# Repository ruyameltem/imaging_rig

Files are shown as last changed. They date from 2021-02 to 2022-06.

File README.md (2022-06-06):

<h1 style="text-align: justify;"><strong>imaging Rig for Microfluidic blood analysiS (RMS)</strong></h1>
<h2 style="text-align: center;">Lights, Camera, Action!</h2>
<p>Rise of the blood and plasma</p>

<p style="text-align: justify;"><strong>Developed by</strong> Edwards lab, University of Reading School of Pharmacy <a href="https://research.reading.ac.uk/biomedical-technology-lab/">Biomedical Technology Lab</a></p>

<p style="text-align: justify;">The imaging rig has been developed to quickly test platelet function for cardiovascular health and disease epidemiology.</p>

<p style="text-align: justify;">This project aims at developing new assays and miniaturised devices to measure the function of the blood cells involved in clotting and thrombus formation- platelets (thrombocytes). The micro capillary film containing small capillaries and made using a melt extrusion process is used to develop new ways of measuring platelet function. We have been testing new detection methods such as using the Raspberry Pi camera.</p>

<p style="text-align: justify;">This system can be used to measure the parameters of liquids such as density and viscosity. By taking time-lapse images, kinetic information of the fluid in the capillary can be obtained. In this way, it is a suitable device not only for blood studies, but also for anyone who wants to work with fluids.</p>

<p style="text-align: justify;">This research shall contribute to the improvement of a new generation with state-of-the-art but affordable point-of-care tests for global utilizations.</p>

<p>You can find the rig's <a title="Technical Specifications" href="https://gitlab.com/ruyameltem/imaging_rig/-/blob/master/Technical%20Specifications.pdf" target="_blank" rel="noopener">Technical Specifications</a></p>

<h3 style="text-align: justify;">Fundamental and 3D-printed parts</h3>
<p><strong>Before you begin,</strong> make sure you have all the necessary parts. You can find all the parts in the <a title="Bill of Materials" href="https://gitlab.com/ruyameltem/imaging_rig/-/blob/master/Bill%20of%20Materials.pdf" target="_blank" rel="noopener">Bill of Materials</a> list.</p>
<p>It is good to have basic skills to use Raspberry Pi, some wiring skills for electronic parts, and designing and printing skills for 3D-printed parts. Do not worry! You can gain skills by watching some short videos and browsing websites. Keep moving forward I added useful links for you. You only need to know how you can use the Raspberry Pi, which is a minicomputer and its pins, how you can wire the "black and red" cables and how to print the designs.</p>
<p>Make sure you have the necessary parts (camera, screen, power supply, SD card, optional: keyboard, mouse) to run the Raspberry pi.</p>
<p>Here are some useful links for Raspberry Pi: <a title="Getting started with Raspberry Pi" href="https://www.raspberrypi.com/dhttps://www.raspberrypi.com/documentation/computers/getting-started.htmlocumentation/computers/getting-started.html" target="_blank" rel="noopener">Getting started with Raspberry Pi</a>, <a title="Documentation: Raspberry Pi" href="https://www.raspberrypi.com/documentation/" target="_blank" rel="noopener">Documentation: Raspberry Pi</a>, <a title="Software: Raspberry Pi" href="https://www.raspberrypi.com/software/" target="_blank" rel="noopener">Software: Raspberry Pi</a></p> 

<p><strong>After collecting the fundamental parts,</strong> you will need to print the 3D printed parts. Download the STL files through the <a title="Design files - OpenSCAD" href="https://gitlab.com/ruyameltem/imaging_rig/-/tree/master/Design_files%20-%20OpenSCAD" target="_blank" rel="noopener">Design files - OpenSCAD</a> page.</p>

<p>You will need the nuts, bolts, etc. to assemble some of the parts. I printed 3D parts with Prusa i3 MK3. It is fine to use another 3D printer. You can tick the support option for some designs. You can change the layer size or any other settings. See below the settings I use:</p>

<p>printer settings</p>
<p>I used the black PLA filament to print all the parts. I just used transparent PLA filament for the test strip holder.</p>
<p>I designed and printed holders to attach all parts (battery, relay, etc.) to the aluminium extrusion. All are available on the design page.</p>
<p>If you have purchased the parts and printed what you need to print, now it is time to assemble them.</p>

<h3 style="text-align: justify;">Assembly Instructions</h3>
<h4 style="text-align: justify;">Assembling the V-Slot aluminium extrusions</h4>
<p>We used 4 20x20mm V-Slot linear rails to create the rectangle at the base. We used a 20x40mm extrusion to attach the servo motor, v-slot gantry plate kit, sample and test strip holders. We used a 20x80mm extrusion to fix the Pi camera and touchscreen. We wanted to be able to change the height of the camera when needed.</p>
<p>We used inside hidden corner, 90-degree cast corner, drop-in tee nuts and hex nuts to combine them. You can find the details in the bill of materials.</p>

<h4 style="text-align: justify;">Assembling the servo motor, gantry plate and strip holder</h4>
<p>The servo motor was attached to the 20x40mm aluminium extrusion by means of the servo bracket. An eccentric horn was placed on the servo in order to make the test strip holder rise and fall as the servo operated.</p>
<p>Servo is controlled by Raspberry Pi via servo six motor kit. The kit is powered by 4 AA batteries.</p>
<p>Useful link for servo six motor kit assembly instruction: <a title="Instructions: servo six board" href="https://cdn.shopify.com/s/files/1/0176/3274/files/instructions_servo_six.pdf?v=1589990518" target="_blank" rel="noopener">servo six board</a></p>

<p>Also, the stripwell holder is mounted on the extrusion. The holder fits a 1 x 12 Stripwell™ Microplate.</p>

<p>The gantry plate was placed on the extrusion so that it was on the upper part of the servo. In addition, the rack holder was mounted on the gantry plate to place the strip holder. Thus, the plate moves up and down by the servo so that it moves the holder.
Useful link for <a title="Gantry plate assembly" href="https://ooznest.co.uk/wp-content/uploads/2018/07/OX-Assembly-Manual.pdf">Gantry plate assembly instructions</a></p>

See figures:
<p>servo assembly</p>

<h4 style="text-align: justify;">Assembling the camera and touchscreen</h4>
<p>The V2 Pi camera was mounted on the Raspberry Pi camera medium plate V2. Following this, the plate was attached to the 20x80mm aluminium extrusion. In addition, the touch screen was attached to the same extrusion by means of 2 touch Pi mounts and 2 universal mounts. Raspberry Pi was mounted on the back of the screen via the Pi case.</p>
<p>Useful links for camera and screen assembly instructions: <a title="Getting started with 7&Prime; touchscreen" href="https://www.okdo.com/getting-started/get-started-with-7-touchscreen-for-raspberry-pi/" target="_blank" rel="noopener">Getting started with 7&Prime; touchscreen</a>, <a title="Getting started with picamera" href="https://projects.raspberrypi.org/en/projects/getting-started-with-picamera" target="_blank" rel="noopener">Getting started with picamera</a></p>

<h4 style="text-align: justify;">Assembling the light sources and relay</h4>
<p>The white LED strips were soldered to the plastic sheet with black and red wires and framed by 4 20x80mm aluminium extrusions. The black wire should be soldered to the minus and the red wire to the positive. 2 holes were drilled on the plastic sheets and the sheets were mounted on the extrusion with screws. The lightbox was also mounted on the main frame.</p>

<p>The light source is controlled by Raspberry Pi via relay.</p>
<p>Useful links for relay assembly instructions and LED wiring: <a title="Relay and Raspberry Pi" href="https://www.electronicshub.org/control-a-relay-using-raspberry-pi/#:~:text=Technically%20speaking%2C%20a%20relay%20is,with%20respect%20to%20Raspberry%20Pi." target="_blank" rel="noopener">Relay and Raspberry Pi</a>, <a title="LED strips" href="https://www.waveformlighting.com/home-residential/how-to-connect-an-led-strip-to-a-power-supply" target="_blank" rel="noopener">LED strips</a></p>

<p>Picture10led</p>

<h3 style="text-align: justify;">Run the Rig</h3>
</p>You only need to place your samples and microfluidic into the system. Then only you will need to run the script.</p>
</p>If you are wondering how the system works, check it out: <a title="Rig" href="https://gitlab.com/ruyameltem/imaging_rig/-/blob/master/Rig.mp4">Rig</a></p>

<p>A short video from an experiment: <a title="Performing an experiment" href="https://gitlab.com/ruyameltem/imaging_rig/-/blob/master/Performing%20an%20experiment.mp4">Performing an experiment</a></p>

<h3 style="text-align: justify;">Software</h3>

<p>To view, edit, and run a Python script, you can use the Thonny which is an integrated development environment (IDE). It is already pre-installed on the Raspberry Pi. Check out the link for the helpful video: <a title="Raspberry Pi OS - Get Started with Thonny IDE" href="https://www.youtube.com/watch?v=GssM7hkwJrc" target="_blank" rel="noopener">Raspberry Pi OS - Get Started with Thonny IDE</a></p>

<p>If you want to update Python and your Raspberry Pi, make sure you type and run the following separately in the command section:</p>
<p>1 - sudo apt update</p>
<p>2 - sudo apt full-upgrade</p>
<p>3 - sudo apt-get update</p>
<p>4 - sudo apt-get install python3</p> 

<p>Note: I did not install the Bullseye edition because the camera system has errors with the last update of Raspberry Pi. But if you want to install and update, you can get help from this video to solve the problem: <a title="Raspberry Pi OS Bullseye Update: New Features &amp; Camera Issues" href="https://www.youtube.com/watch?v=0kr_yS9OhLM" target="_blank" rel="noopener">Raspberry Pi OS Bullseye Update: New Features &amp; Camera Issues</a></p>

<p>If you want to use the scripts separately, there are separate scripts for recording video, controlling the LED with a relay, and taking time-lapse images with a date stamp.</p>
<p>But if you want to download and use it directly, the script file you will run is called "Imaging Rig".</p>
<p>Here are the Python scripts you need: <a title="Software" href="https://gitlab.com/ruyameltem/imaging_rig/-/tree/master/Software">Software</a></p>
<p>It is good to have basic Python skills to make some changes on the scripts.</p>

<p>For any questions, please contact me: <a title="r.sariyer@pgr.reading.ac.uk" href="mailto:r.sariyer@pgr.reading.ac.uk">r.sariyer@pgr.reading.ac.uk</a></p>

<h3 style="text-align: justify;">The Rig</h3>
<p style="text-align: justify;">The device is shown below.</p>
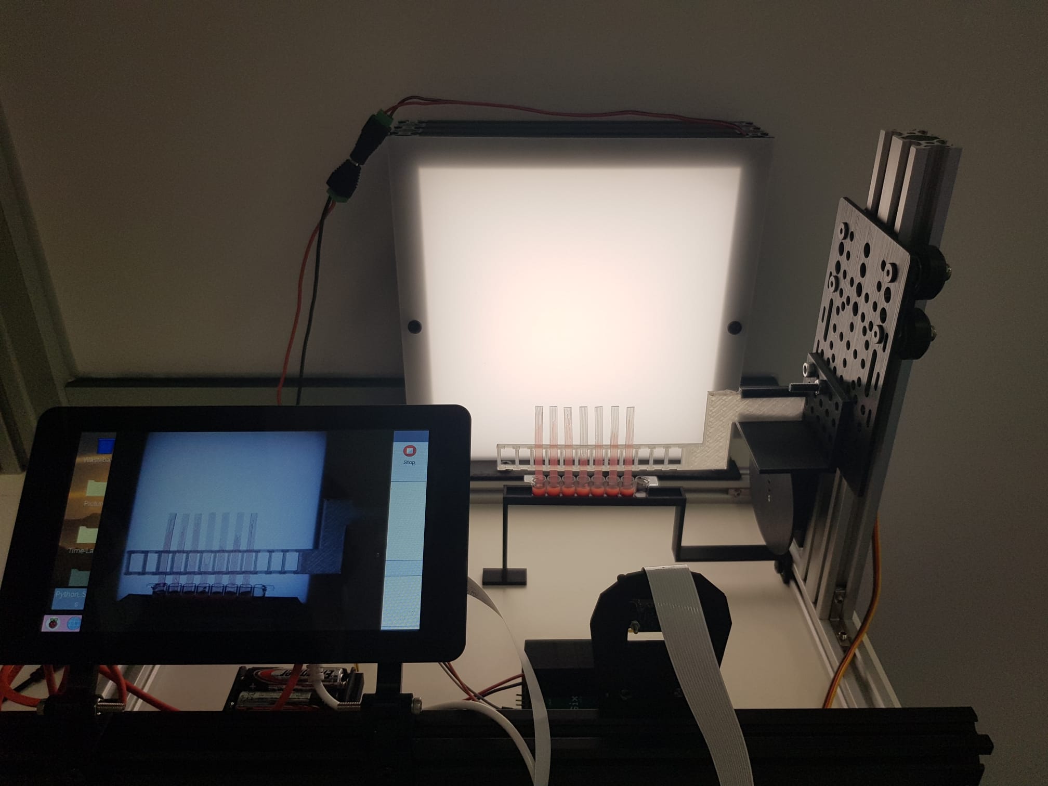
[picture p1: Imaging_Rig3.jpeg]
Imaging Rig
<h2 style="text-align: center;"></h2>
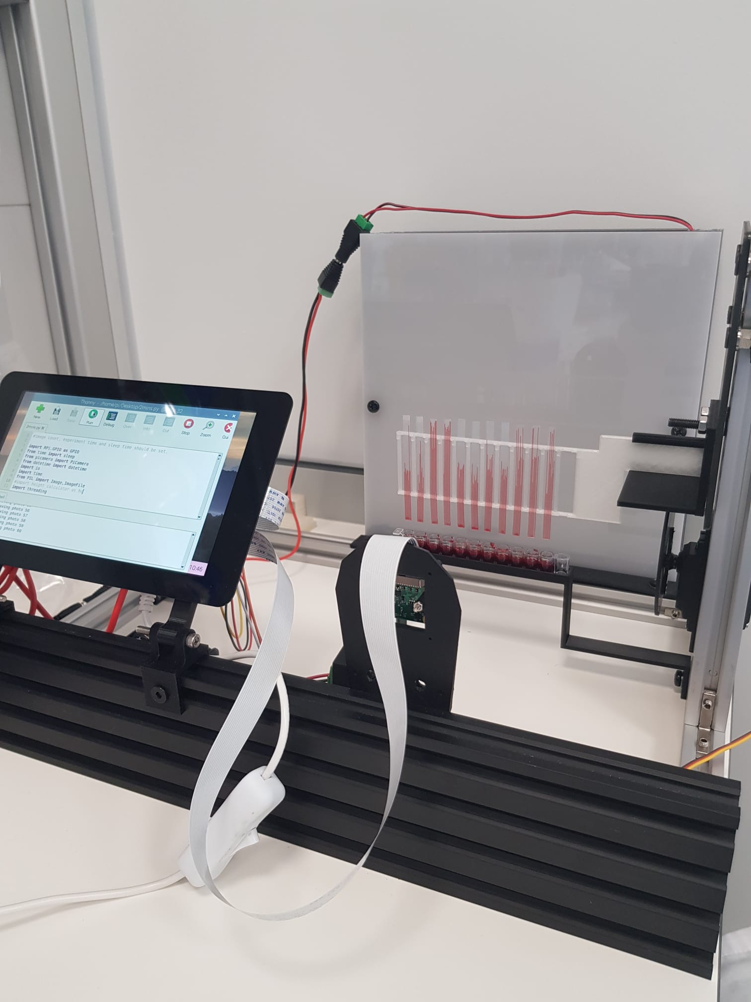
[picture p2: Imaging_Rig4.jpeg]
Imaging Rig 2
<h2 style="text-align: center;"></h2>
<p style="text-align: justify;">The top view of the rig:</p>

<p>The rig gives images like the following one:</p>
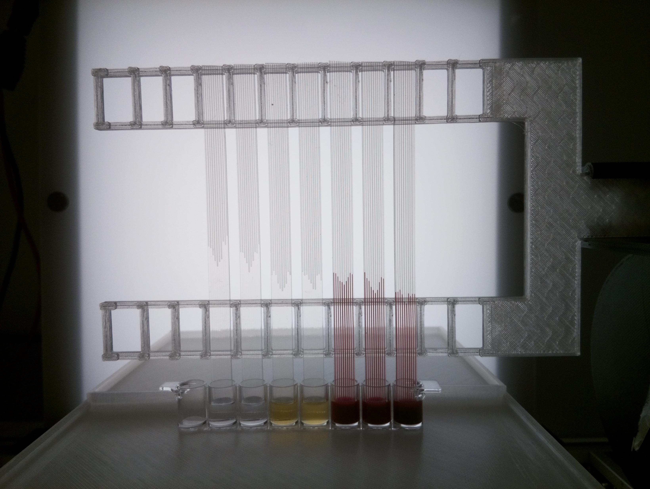
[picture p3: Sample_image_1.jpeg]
Rise of the blood and plasma




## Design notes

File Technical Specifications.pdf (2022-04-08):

This is an open-source robotic microfluidic blood analysis using Raspberry Pi.

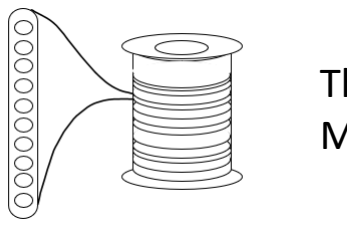
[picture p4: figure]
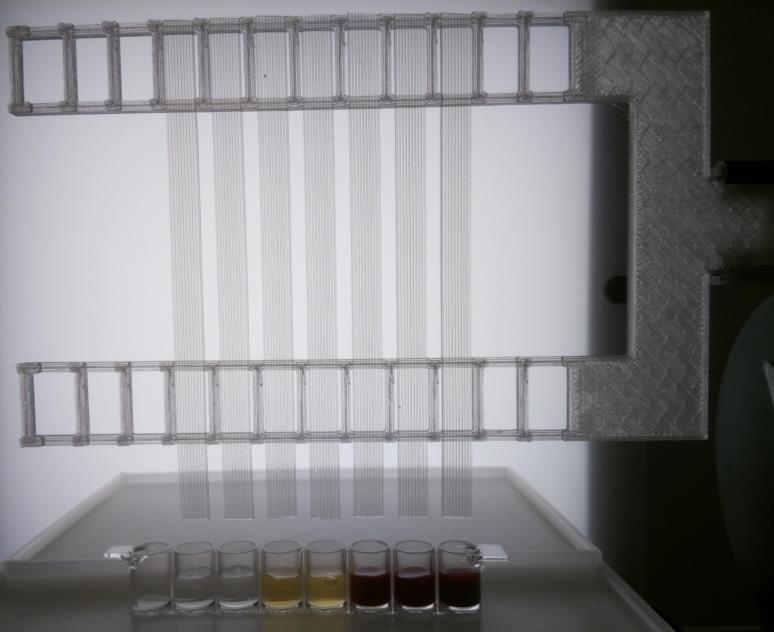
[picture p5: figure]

A light source is built using white LEDs. It is suitable for colorimetric use.

### Technical Specifications:

The test strips are melt-extruded fluoropolymer MCF containing 10 microcapillaries.

A strip holder contains 12 strips.

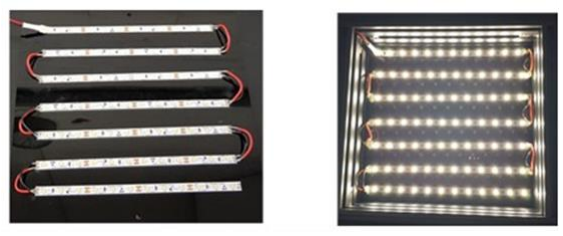
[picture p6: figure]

Opal acrylic light diffuser sheet and black cast acrylic sheet were used. LED strips were connected to each other with black and red wires. And the strips were glued with silicone on the black sheet.

The sheets were then fixed to V-slot aluminium linear rail extrusions. The light source is controlled by a grove single relay.

Technical Specifications:

Initially, a handmade LED turns on by controlling a relay, after that a servo motor via the gantry plate and wheels dip the strip holder into the blood sample which moves into the capillaries by capillary action and after the test is completed the strip holder goes back and the LED turns off.

The servo motor needs 4 batteries. In the meantime, a raspberry pi camera V2 takes images during the experiment.

This camera can take between 6 and 8 images within 1 second. Its resolution is 3280x2464.

Taking the images can be previewed on the touchscreen and the test can be started by clicking run on the script via touchscreen.

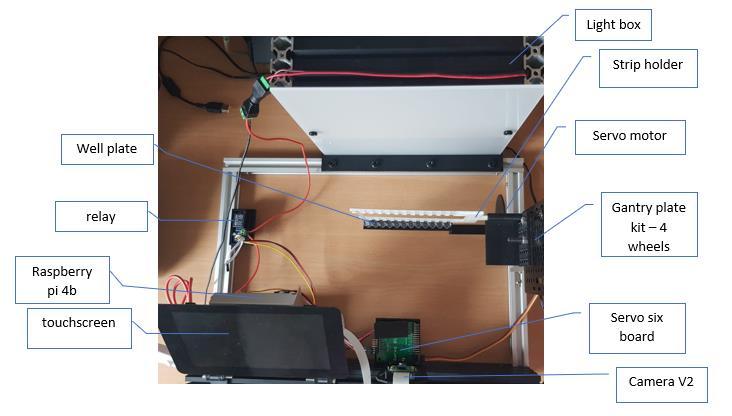
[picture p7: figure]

There is only one script that can control the relay (LED), the servo motor and the camera. With the one-click, the test can be done. The python script has instructions about what the script does and how to change features such as camera resolution, fps, experiment time etc.

After the images are taken, the calculation part begins. From the photos taken in first step, the rise of the blood sample and velocity are calculated, and the data are saved.

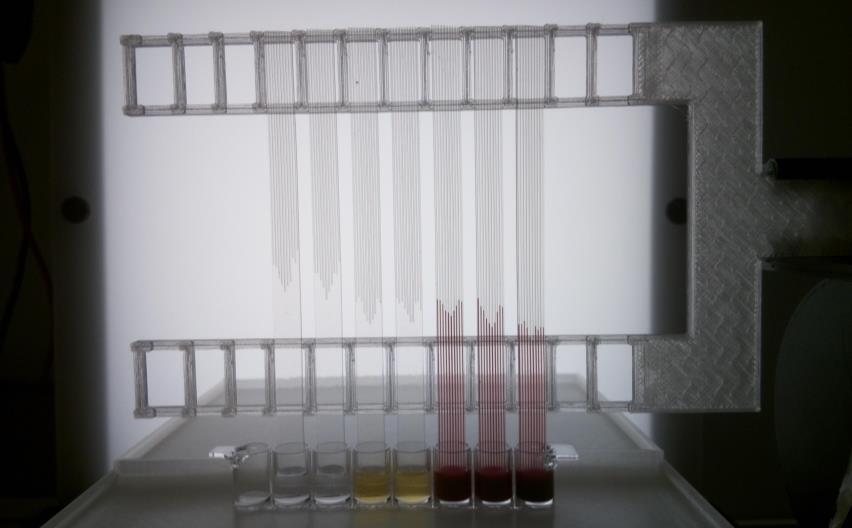
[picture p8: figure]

The rig gives image like the following:

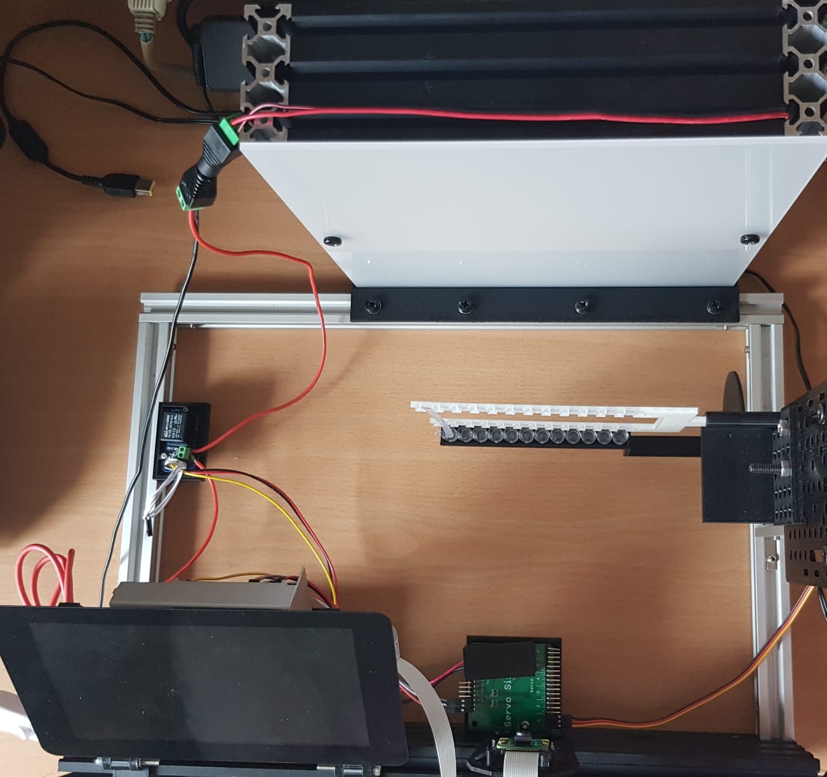
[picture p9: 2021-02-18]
Imaging_Rig.jpeg

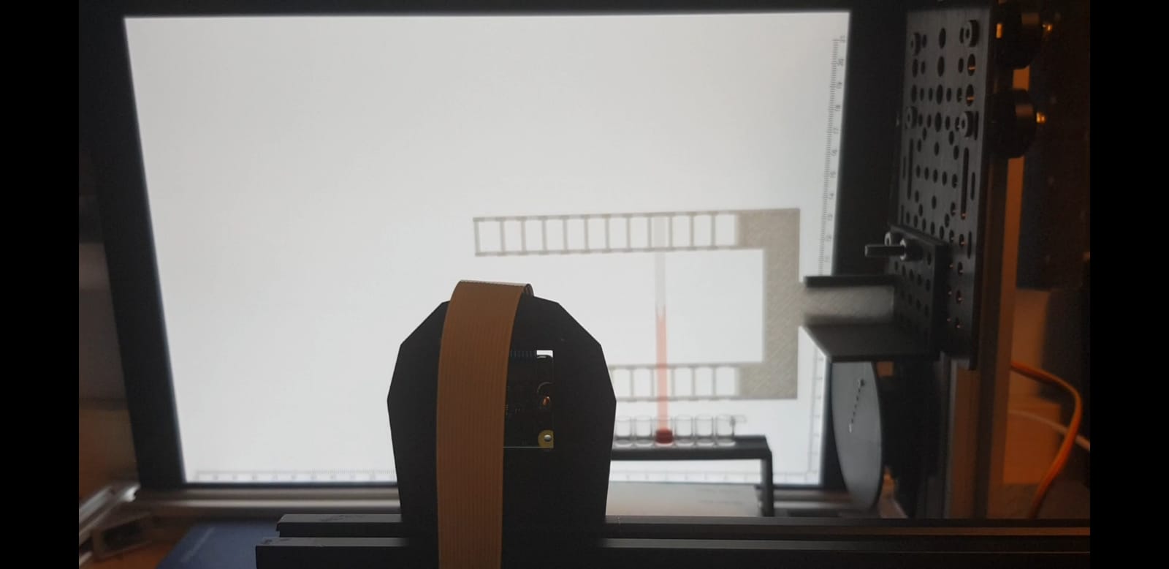
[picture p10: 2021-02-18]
Imaging_Rig_2.jpeg

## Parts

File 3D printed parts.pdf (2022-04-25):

3D-printed parts

For the design of 3D parts, check it out: Design files
- camera holder by Al Edwards
- rack holder by Al Edwards
- microplates holder by Ruya Meltem Sariyer
- ladder comb modified by Ruya Meltem Sariyer
- servo holder modified by Ruya Meltem Sariyer
- raspberry pi camera holder modified by Al Edwards
- eccentric horn modified by Ruya Meltem Sariyer
- 12 well plate holder by Ruya Meltem Sariyer
- strip holder two side by Ruya Meltem Sariyer
- battery holder by Ruya Meltem Sariyer
- relay holder by Ruya Meltem Sariyer
- LED box holder by Ruya Meltem Sariyer
- servo six board holder by Ruya Meltem Sariyer
- Touchscreen mount for 2020 extrusion by Wursterland is licensed under the Creative Commons - Attribution - Non-Commercial license. (2*touchpi mount, 2*universal 2020 mount)
https://www.thingiverse.com/thing:2790206
- Servo mounting bracket bywsolstice69 is licensed under the Creative Commons - Attribution - Share A like license. https://www.thingiverse.com/thing:9915
- 1/4 scale servo bracket by rlspell is licensed under the Creative Commons - Attribution - Share A like license. https://www.thingiverse.com/thing:13850
- Linear Servo Actuators by potentprintables is licensed under the Creative Commons - Attribution - Non-Commercial license.
https://www.thingiverse.com/thing:3170748

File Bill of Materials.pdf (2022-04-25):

90 Degree Cast Corner | Ooznest | | 1.5
screws (servo - mini screw) | | 2
M1 screws | Ooznest | 2
M3 screws | Ooznest | 2
M5 screws | Ooznest
Inside Hidden Corner | Ooznest | 6 | 3 | 18
M5 Drop In Tee Nuts | Ooznest | | 0.26
M1 Hex Nuts | Ooznest | 2
M3 Hex Nuts | Ooznest | 2
M5 Hex Nuts | Ooznest
Servo Six Motor Kit for Raspberry Pi | CPC | 1 | 10.95 | 10.95
Servo, Standard | CPC | 1 | 15.63 | 15.63
Energizer MAX® Alkaline AA Batteries | ASDA | 4 | | 2.4
Raspberry Pi 4 4gb Mode B Starter Kit | OKDO | 1 | 99 | 99
Raspberry Pi Camera V2 | CPC | 1 | 22.29 | 22.29
Raspberry Pi 7" Touch Screen Display | CPC | 1 | 48.39 | 48.39

plastic sheet black (240x250mm)
plastic sheet (240x250mm)
V-Slot Linear Rail (20x40mm) (200mm) | Ooznest | 2 | 2.52 | 5.04
V-Slot Linear Rail (20x40mm) (250 mm) | Ooznest | 2 | 3.15 | 6.3
Grove single relay | Cool Components 1 | | 2.42 | 2.42
Grove connector jumpers female | Cool Components 1 | | 3.19 | 3.19
DC Barrel Jack Adapter - Female | Cool Components 2 | | 3.22 | 6.44
DC Barrel Jack Adapter - Male | Cool Components 1 | | 2.39 | 2.39
LED strip

Raspberry Pi The Rig Light box

### The Rig: £ 56.6, Raspberry Pi: £ 198.6, Light box: £ 25.7 TOTAL: £ 281.1

Item | Source | Qty. | Unit Cost | Total Cost
V-slot gantry plate kit | Ooznest | 1 | 30.5 | 30.5
V-Slot Linear Rail - V-slot aluminium linear rail extrusions: | | | | 0
20x20 250 mm | Ooznest | 2 | 2.5 | 5
20x20 415 mm | Ooznest | 1 | 2.99 | 2.99
20x80 415 mm | Ooznest | 1 | 0.025 | 0.025
20x40 270 mm | Ooznest | 1 | 0.12 | 0.12

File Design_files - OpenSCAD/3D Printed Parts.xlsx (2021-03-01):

camera holder by Al Edwards
rack holder by Al Edwards
microplates holder by Ruya Meltem Sariyer
ladder comb modified by Ruya Meltem Sariyer
servo holder modified by Ruya Meltem Sariyer
raspberry pi camera holder modified by Al Edwards
eccentric horn modified by Ruya Meltem Sariyer
12 well plate holder by Ruya Meltem Sariyer
strip holder two side by Ruya Meltem Sariyer
battery holder by Ruya Meltem Sariyer
relay holder by Ruya Meltem Sariyer
LED box holder by Ruya Meltem Sariyer
servo six board holder by Ruya Meltem Sariyer
Touchscreen mount for 2020 extrusion byWursterlandis licensed under theCreative Commons - Attribution - Non-Commerciallicense. | https://www.thingiverse.com/thing:2790206
2*touchpi mount
2*universal 2020 mount
Servo mounting bracket bywsolstice69is licensed under theCreative Commons - Attribution - Share Alikelicense. | https://www.thingiverse.com/thing:9915
1/4 scale servo bracket byrlspellis licensed under theCreative Commons - Attribution - Share Alikelicense. | https://www.thingiverse.com/thing:13850
Linear Servo Actuators bypotentprintablesis licensed under theCreative Commons - Attribution - Non-Commerciallicense. | https://www.thingiverse.com/thing:3170748

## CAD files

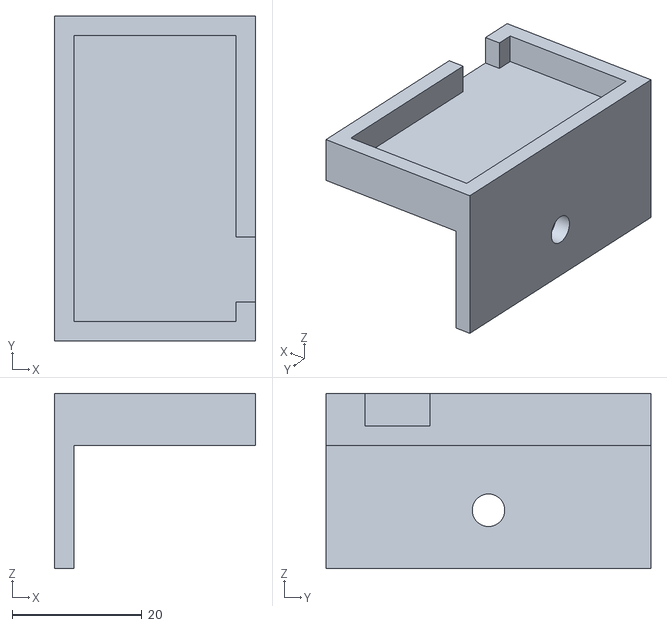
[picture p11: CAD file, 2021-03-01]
Design_files - OpenSCAD/relay_holder_Ruya.stl
31.0 x 50.0 x 27.0

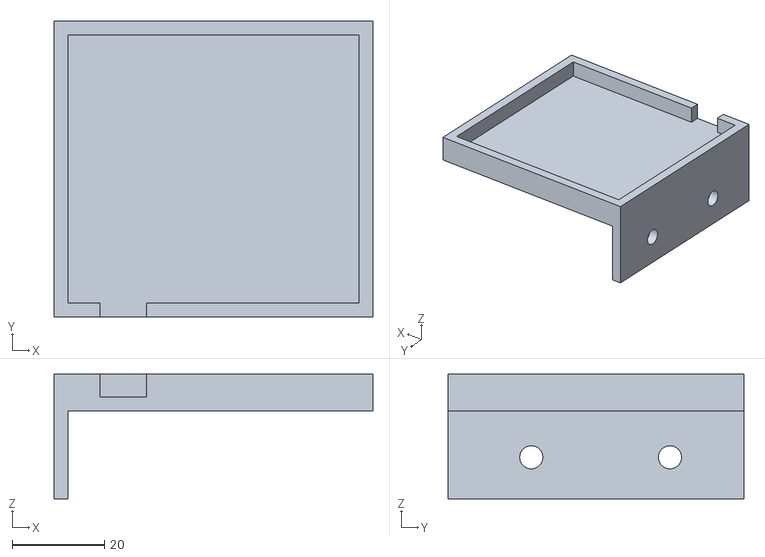
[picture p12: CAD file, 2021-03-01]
Design_files - OpenSCAD/battery_holder_Ruya.stl
69.0 x 64.0 x 27.0

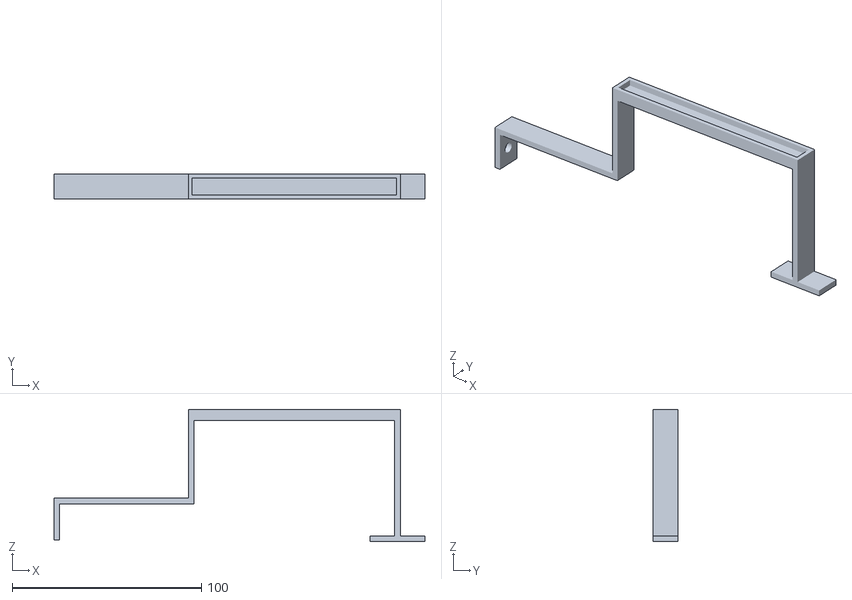
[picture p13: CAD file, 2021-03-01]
Design_files - OpenSCAD/stripwell_holder_12_17.02.21_Ruya.stl
196.0 x 13.0 x 70.0

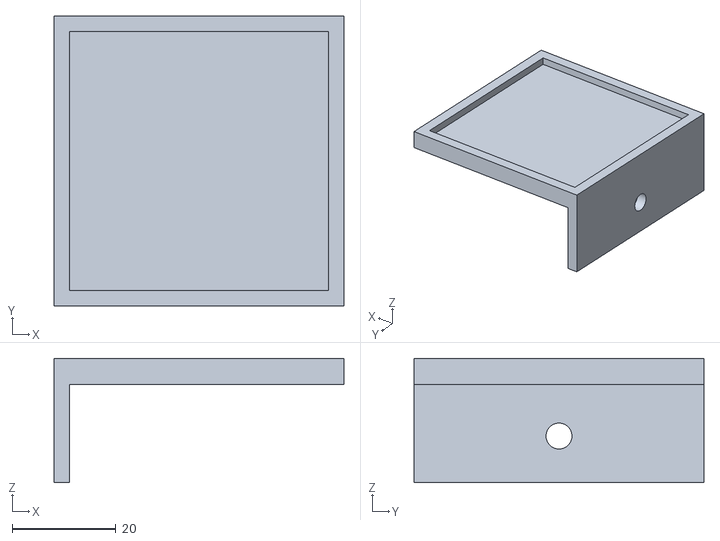
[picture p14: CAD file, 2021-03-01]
Design_files - OpenSCAD/servo_six_board_holder_Ruya.stl
56.0 x 56.0 x 24.0

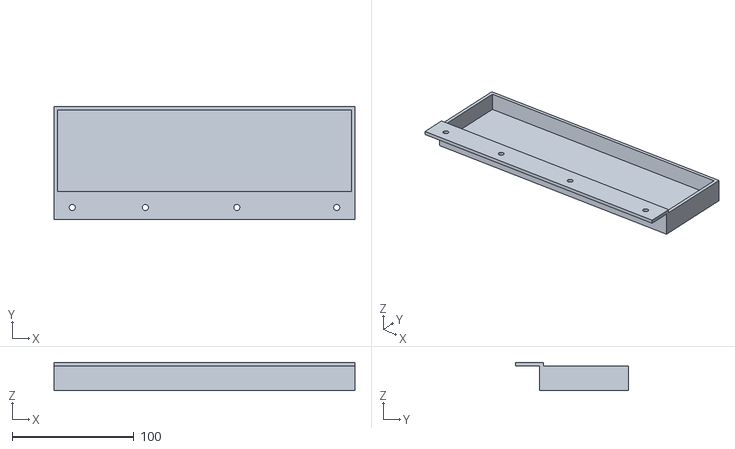
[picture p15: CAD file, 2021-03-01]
Design_files - OpenSCAD/LED_holder.stl
247.0 x 93.0 x 23.0

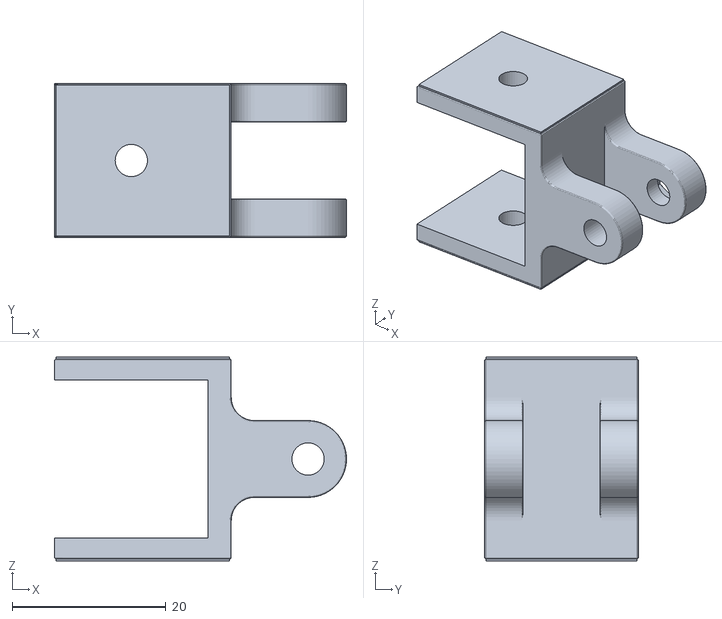
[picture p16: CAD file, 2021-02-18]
Design_files - OpenSCAD/Universal_2020_mount.stl
38.0 x 20.0 x 26.5

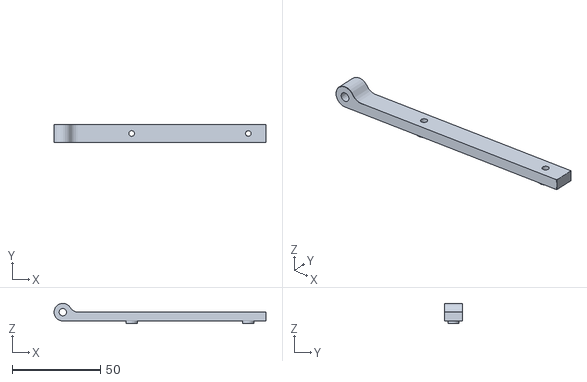
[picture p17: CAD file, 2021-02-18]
Design_files - OpenSCAD/TouchPi_mount.stl
120.0 x 10.0 x 11.5

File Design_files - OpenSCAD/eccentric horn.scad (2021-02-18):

//plan to have servo horn with 15mm offset to make cam


module eccentrichorn(sized=80,offset=15){
    difference(){
    translate([offset/2,0,0])cylinder(h=2,d=sized,$fn=120);
    
translate([0,0,-50])        cylinder(d=2,h=100,$fn=12);
        
         for (i = [1:3]) { 
            translate([i*5,0,-50]) cylinder(d=2.5,h=100,$fn=12);
mirror([1,0,0])translate([i*5,0,-50]) cylinder(d=2.5,h=100,$fn=12);
             }
        
    }
}


eccentrichorn();

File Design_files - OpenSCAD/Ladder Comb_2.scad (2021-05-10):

difference(){
union(){
difference () {
union () {


difference () {
translate ([-3,-3,0])cube ([113, 2, 3]);


translate ([2,-75,2])cube ([4.49,95,3]);

translate ([11,-5,2])cube ([4.4,20,3]);
    translate ([20,-5,2])cube ([4.49,20,3]);
    translate ([29,-5,2])cube ([4.49,20,3]);
    translate ([38,-5,2])cube ([4.49,20,3]);
    translate ([47,-5,2])cube ([4.49,20,3]);
    translate ([56,-5,2])cube ([4.49,20,3]);
    translate ([65,-5,2])cube ([4.49,20,3]);
    translate ([74,-5,2])cube ([4.49,20,3]);
    translate ([83,-5,2])cube ([4.49,20,3]);
    translate ([92,-5,2])cube ([4.49,20,3]);
    translate ([101,-5,2])cube ([4.49,20,3]);

}


difference () {
translate ([-3,15,0])cube ([113, 24, 3]);


translate ([2,5,2])cube ([4.49,38,5]);

translate ([11,5,2])cube ([4.49,38,5]);
    translate ([20,5,2])cube ([4.49,38,3]);
    translate ([29,5,2])cube ([4.49,38,3]);
    translate ([38,5,2])cube ([4.49,38,3]);
    translate ([47,5,2])cube ([4.49,38,3]);
    translate ([56,5,2])cube ([4.49,38,3]);
    translate ([65,5,2])cube ([4.49,38,3]);
    translate ([74,5,2])cube ([4.49,38,3]);
    translate ([83,5,2])cube ([4.49,38,3]);
    translate ([92,5,2])cube ([4.49,38,3]);
    translate ([101,5,2])cube ([4.49,38,3]);
}

    translate ([-3,-3,0]) cube ([2,42,3]);
 translate ([8,-3,0]) cube ([2,42,3]);
 translate ([17,-3,0]) cube ([2,42,3]);
   translate ([26,-3,0]) cube ([2,42,3]);
 translate ([35,-3,0]) cube ([2,42,3]);
 translate ([44,-3,0]) cube ([2,42,3]);
translate ([53,-3,0]) cube ([2,42,3]);
 translate ([62,-3,0]) cube ([2,42,3]);
 translate ([71,-3,0]) cube ([2,42,3]);
   translate ([80,-3,0]) cube ([2,42,3]);
 translate ([89,-3,0]) cube ([2,42,3]);
 translate ([98,-3,0]) cube ([2,42,3]);
translate ([108,-3,0]) cube ([2,42,3]);

}

translate ([-5,2,2]) cube ([120,35,3]);

}

}

translate ([-1,-1,0])cube ([9,38,3]);
translate ([10,-1,0])cube ([7,38,3]);
translate ([19,-1,0])cube ([7,38,3]);
translate ([28,-1,0])cube ([7,38,3]);
translate ([37,-1,0])cube ([7,38,3]);
translate ([46,-1,0])cube ([7,38,3]);
translate ([55,-1,0])cube ([7,38,3]);
translate ([64,-1,0])cube ([7,38,3]);
translate ([73,-1,0])cube ([7,38,3]);
translate ([82,-1,0])cube ([7,38,3]);
translate ([91,-1,0])cube ([7,38,3]);
translate ([100,-1,0])cube ([8,38,3]);

}

translate ([-28,-3,0])cube ([25, 42, 3]);


translate ([-28,-12,0])cube ([15, 17, 3]);
translate ([-28,5,0])cube ([15, 17, 3]);


translate ([-68,-12,0])cube ([40, 19.1, 3]);

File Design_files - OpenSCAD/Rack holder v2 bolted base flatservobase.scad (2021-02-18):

//clip for
//19mm x 3mm thick handled holder for MCF 'train track' about 40mm long


thick=3;
wide=19;
$fn=12;
clearance=0.2; //this is minkowski around device

difference(){
    
    union(){
translate([0,0,0]) cube([thick+53,wide+25,4]);  //base plate 
translate([0,0,0]) cube([thick+2,wide+4,40]); //main holder
//translate([thick+2,2,0]) cylinder(h=40,d=6,$fn=12); //main rods
translate([thick+2,0,0]) cube([50,3,40]);      //plate to replace one rod, for servo waggling
translate([thick+2,wide+2,0]) cylinder(h=40,d=6,$fn=12); //main rods
    
        }
    
    //subtract core for grabbing flex
hull(){
translate([-1,wide/2+2,40]) rotate([0,90,0]) cylinder(d=wide/2.3,h=10);
translate([-1,wide/2+2,10]) rotate([0,90,0]) cylinder(d=wide/1.5,h=10);    
}
//MCF holder- this is the actual object to be held

hull(){
minkowski(){
translate([2,2,2]) cube([thick,wide,44]);
sphere(r=clearance);
}
translate([wide/3,wide/4+2,5]) cube([thick,wide/2,44]);

}
//translate([1,1,0]) cube([thick,wide+2,14]); //THIS WAS IN BASE OF CLIP 

//hole grid for mounting
for (i = [0:4]) {
    for (j = [0:5]) {
  translate([i*10+10,j*10+8,-1]) cylinder(d=5,h=20);
    }
}

}

module bracket(){
difference(){
union(){
translate([0,0,0]) cube([25,25,4]);  //base plate 
translate([0,0,0]) cube([4,25,20]); //bracket
}
for (i = [0:2]) {
    for (j = [0:3]) {
  translate([i*5+10,j*5+5,-1]) cylinder(d=2.5,h=20);
    }
}
}

}


//translate([30,0,0]) bracket();

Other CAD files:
Design_files - OpenSCAD/Raspberry pi camera medium plate v2 v-slot lugs.scad
Design_files - OpenSCAD/Raspberry pi camera mounts 40mm wide mounting.scad
Design_files - OpenSCAD/Raspberry pi camera mounts for servo.scad
Design_files - OpenSCAD/servo_bracket thingiverse.scad
Design_files - OpenSCAD/strip_holder_two_side.scad
Design_files - OpenSCAD/stripwell_holder_12.scad

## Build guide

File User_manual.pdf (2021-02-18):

### User Manual:

Blood samples should be filled into the microplate. 12 different samples can be filled. In addition to this, the strips should be placed on the strip holder. To start the test, the desired features such as experiment time and resolution etc. should be set and the program should be run.

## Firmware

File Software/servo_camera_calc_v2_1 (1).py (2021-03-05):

#image count, experiment time and sleep time should be set.

import RPi.GPIO as GPIO
from time import sleep
from picamera import PiCamera
from datetime import datetime
import io
import time 
from PIL import Image,ImageFile 
#import height_calculator as hc
import threading 

class create_before (threading.Thread):
   def __init__(self, threadID, name, counter):
      threading.Thread.__init__(self)
      self.threadID = threadID
      self.name = name
      self.counter = counter
   def run(self): 
      record() 
      
class create_after (threading.Thread):
   def __init__(self, threadID, name, counter):
      threading.Thread.__init__(self)
      self.threadID = threadID
      self.name = name
      self.counter = counter
   def run(self):
       after_record()


names = []

#the second takes for from servo's starting going down and experiement's ending
EXPERIMENT_TIME = 8

#servo step count
DISTANCE = 12

#servo movement
IS_SERVO_MOVED = 2

#servo downtime
SERVO_DOWN_TIME = DISTANCE + IS_SERVO_MOVED

#maximum resolution
RESOLUTION = (3280,2464)

#maximum picture
FPS = 10

#picture count
IMAGE_COUNT = FPS * (EXPERIMENT_TIME + SERVO_DOWN_TIME)

def outputs():
    global names, IMAGE_COUNT
    
    stream = io.BytesIO()
    
    for i in range(IMAGE_COUNT) : 
        # This returns the stream for the camera to capture to
        yield stream
        stream.seek(0)
        names.append([datetime.utcnow().strftime('%Y-%m-%d-%H:%M:%S.%f'),stream.getvalue()])
        # Once the capture is complete, the loop continues here
        # (read up on generator functions in Python to understand
        # the yield statement). Here you could do some processing
        # on the image...
        #stream.seek(0)
        #img = Image.open(stream)
        # Finally, reset the stream for the next capture
        stream.truncate()
        print('image',i,datetime.utcnow().strftime('%Y-%m-%d-%H:%M:%S.%f')) 
    

def record():
    global RESOLUTION,FPS

    print("LED is about to open")
    #LED will be open
    led1 = 21 #GPIO pin to connect to relay
    
    GPIO.setwarnings(False)
    GPIO.setmode(GPIO.BCM)
    GPIO.setup(led1, GPIO.OUT)

    GPIO.output(led1, True)    
    time.sleep(1)
    
    print('taking pictures')
    
    camera = PiCamera() 
    camera.start_preview()
    #start capture     
    camera.resolution=RESOLUTION
    camera.framerate = FPS
    camera.rotation = 180
    
    camera.capture_sequence(outputs(), 'jpeg', use_video_port=True)
    #Experiment ended stop the camera
    camera.stop_preview()
    print('capturing ended')

    #LED is stopping
    GPIO.setmode(GPIO.BCM)
    GPIO.setup(led1, GPIO.OUT)
    GPIO.output(led1, False)
    time.sleep(2)
    print('LED stopped')

    #Start the calculation

    i=1
    results = []

    #change this settings according to the environment

    ENV_RED = 75
    ENV_COLORS = 75
    ENV_STABILITY = 20

    #calculate heights for every picture

    print('calculating started')
      
    i=0
    for frameData in names:
        byteImg = frameData[1]
        byteImg = io.BytesIO(byteImg)
        byteImg = Image.open(byteImg) 
        filename = "/home/pi/Desktop/Time-Lapse/test/" + frameData[0] + ".jpeg"
        byteImg.save(filename, 'JPEG')
        print('saving photo',i)
        i+=1
        '''
        try:
            results.append(hc.main(ENV_RED,ENV_COLORS,ENV_STABILITY,byteImg))
        except:
            print("error happened on :",
                  "image_number = "+str(i),
                  "image_name = "+frameData[0])
            continue
            
        print('calculated',i)
        i+=1
        '''

    #save the results

    '''
    with file as open('/home/pi/Desktop/Time-Lapse/test/'+datetime.utcnow().strftime('%Y-%m-%d-%H:%M:%S.%f')+'.txt','w'):
        file.write(results)
    '''
 

def after_record():
    global DISTANCE,IS_SERVO_MOVED,EXPERIMENT_TIME
        
    servoPIN = 17
    GPIO.setmode(GPIO.BCM)
    GPIO.setup(servoPIN, GPIO.OUT)

    p = GPIO.PWM(servoPIN, 50) # setting pin as 17 and choosing 50Hz PWM
    duty = 0

    #initialising servo
    p.start(duty)
    duty  = 12.0
    while 0 < duty:
        duty-=3.0
        p.ChangeDutyCycle(duty)
        sleep(0.1)
        
    #preparing
    sleep(4)
    
    print('servo to down')
    #servo to down 
    while duty < DISTANCE:
        duty+=1
        p.ChangeDutyCycle(duty) 
                 
    sleep(IS_SERVO_MOVED-1.5)
    p.stop()

    print('servo on down')

    #Experiment started
    sleep(28)
    
    p.start(duty)    
    #servo to top
    while duty < 100:
        duty+=13.0
        if duty > 89:
            print("servo to top")
            p.stop()
        if duty < 89:
            p.ChangeDutyCycle(duty)
        sleep(0.1)

    #is servo on top
    sleep(IS_SERVO_MOVED)

    print('servo on top')

    #stop the servo
    p.stop()

     
thread1 = create_before(1,'1',1)
thread2 = create_after(2,'2',2)

thread1.start()
thread2.start()

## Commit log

2021-02-18 Upload Bills of Materials
    [Bill_of_Materials.xlsx]
2021-02-18 Design files - OpenSCAD
    [3D_Printed_Parts.xlsx, Rack holder v2 bolted base flatservobase.scad, Raspberry pi camera mounts 40mm wide mounting.scad, TouchPi_mount.stl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]
2021-02-18 servo - taking images
2021-02-28 The script for the camera v2, servo and LED box - servo doesn't go to the top (problem!)
2021-03-01 design folder - holder for battery, relay, servo six board, LED and 12 well plate
    [LED_holder.stl, battery_holder_Ruya.stl, relay_holder_Ruya.stl, servo_six_board_holder_Ruya.stl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]
2021-03-01 Deleted stripwell_holder_12_17.02.21_Ruya.stl, servo_six_board_holder_Ruya.stl, battery_holder_Ruya.stl, relay_holder_Ruya.stl files
    [battery_holder_Ruya.stl, relay_holder_Ruya.stl, servo_six_board_holder_Ruya.stl, stripwell_holder_12_17.02.21_Ruya.stl]
2021-03-01 Deleted LED_holder.stl
    [LED_holder.stl]
2021-03-01 Holders for relay, battery, servo six board, LED and 12 well plate
    [LED_holder.stl, battery_holder_Ruya.stl, relay_holder_Ruya.stl, servo_six_board_holder_Ruya.stl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]
2021-03-01 Update Design_files - OpenSCAD/Raspberry pi camera medium plate v2 v-slot lugs.scad, Design_files - OpenSCAD/Raspberry pi camera mounts for servo.scad files
    [Raspberry pi camera medium plate v2 v-slot lugs.scad, Raspberry pi camera mounts for servo.scad]
2021-03-01 Deleted Design_files - OpenSCAD/3D_Printed_Parts.xlsx
    [3D_Printed_Parts.xlsx]
2021-03-01 Update Design_files - OpenSCAD/3D Printed Parts.xlsx
    [3D Printed Parts.xlsx]
2021-03-02 Deleted Software/servo_camera_calc_v2_1.py
2021-03-05 Update servo_camera_calc_v2_1 (1).py
2021-05-10 New design for the strip holder (long version for 6 cm MCF)
    [Ladder Comb_2.scad]
2021-05-10 New design for strip holder (for 6cm MCF)
    [Ladder Comb_2.scad]
2022-04-06 Update Sample images 1
2022-04-06 Update Sample_image_1 Deleted Sample images 1
2022-04-06 Deleted Sample_image_1
2022-04-08 Update Bill of Materials.pdf Deleted Bill_of_Materials.xlsx
    [Bill_of_Materials.xlsx]
2022-04-25 Deleted Bill of Materials.pdf
2022-04-25 Update 3D printed parts.pdf, Bill of Materials.pdf
